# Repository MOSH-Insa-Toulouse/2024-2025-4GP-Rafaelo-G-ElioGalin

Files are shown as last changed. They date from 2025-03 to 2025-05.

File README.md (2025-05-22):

# 2024-2025-4GP-Rafaelo-G-ElioGalin

# Projet Capteur

## Somaire

- [Principe du Projet](#principe-du-projet)
- [Livrables](#livrables)
- [LTSpice](#ltspice)
- [Réalisation informatique du PCB sur KiCAD](#Realisation-informatique-du-pcb-sur-kicad)
- [Réalisation physique du PCB](#Réalisation-physique-du-PCB)
- [Code Arduino](#code-arduino)
- [Application](#application)
- [Datasheet](#datasheet)
- [Conclusion](#conclusion)
- [Auteurs](#auteurs)

## Contexte du Projet
Dans le Cadre du cours " Du capteur au banc de test", qui se base sur l'article "Pencil Drawn Strain Gauges and Chemiresistors on Paper" de Cheng-Wei Lin et al., les étudiants sont invités à caractériser un capteur particulier composé d'une simple feuille de papier et d'une couche de graphite. Cette couche de graphite joue le rôle d'une resistance variable qui dépend de la flexion du papier. Le but de ce projet est de réaliser un banc de test permettant d'étudier les variations de cette résistance en fonction de la déformation du capteur.

## Livrables

- Un PCB contenant différents modules se reliant à une carte Arduino UNO.
- Un code Arduino pour pouvoir controler les différents modules sur le PCB.
- Un application permettant la connection au PCB par Bluetooth.
- Une datasheet du capteur graphite.

## LTSpice 

La résistance du capteur graphite est de l'ordre du Méga Ohm et ne peut donc pas se mesurer simplemen. Nous utilison une alimentation 5V, nous avons donc :
U = R * I --> I = U/R --> I très faible.

Pour pouvoir obtenir des valeurs acceptables, nous avons réalisé un circuit amplificateur à transimpédance : 

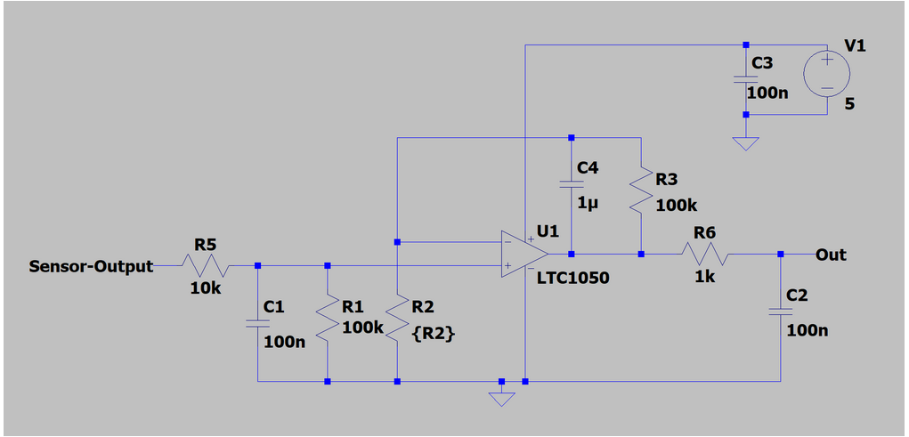
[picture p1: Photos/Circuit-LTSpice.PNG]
LTSpice-shema


Pour l'amplificateur opérationnel nécessaire au circuit, nous avons choisi le LTC1050 pour sa capacité à accepter un courant d'entrée faible et un offset de tension bas.

Afin d'améliorer le rapport Signal/Bruit, nous avons ajouté trois filtres : 

- filtre passe bas passif en entrée (R1,C1) avec une fréquence de coupure fc1 = 16Hz.
- filtre passe bas actif couplé à l'amplificateur opérationnel (R3,C4) avec une Fréquence de coupure fc2 = 1.6Hz. Ce filtre permet de s'isoler du bruit 50Hz du réseau électrique.
- filtre en sortie (R6,C2), avec une fréquence de coupure fc3 = 1.6kHz. Ce filtre permet de s'affranchir du bruit généré par notre circuit.

## Réalisation informatique du PCB sur KiCAD

Pour la réalisation du PCB, nous avons utilisé le logiciel KiCAD 6.0. Ce logiciel permet de créer le cricuit électrique ainsi que le PCB grâce à ses nombreuses librairies de composants.

La réalisation du PCB implique l'utilisation de différents modules qu'il faut pouvoir afficher sur le shéma : 

- Un module Bluetooth HC-05.
- Un écran OLED
- Un potentiomètre digital qui remplace la résistance R2 de notre circuit LTSpice.

Dans un premier temps, nous avons effectuée le shéma électrique : 

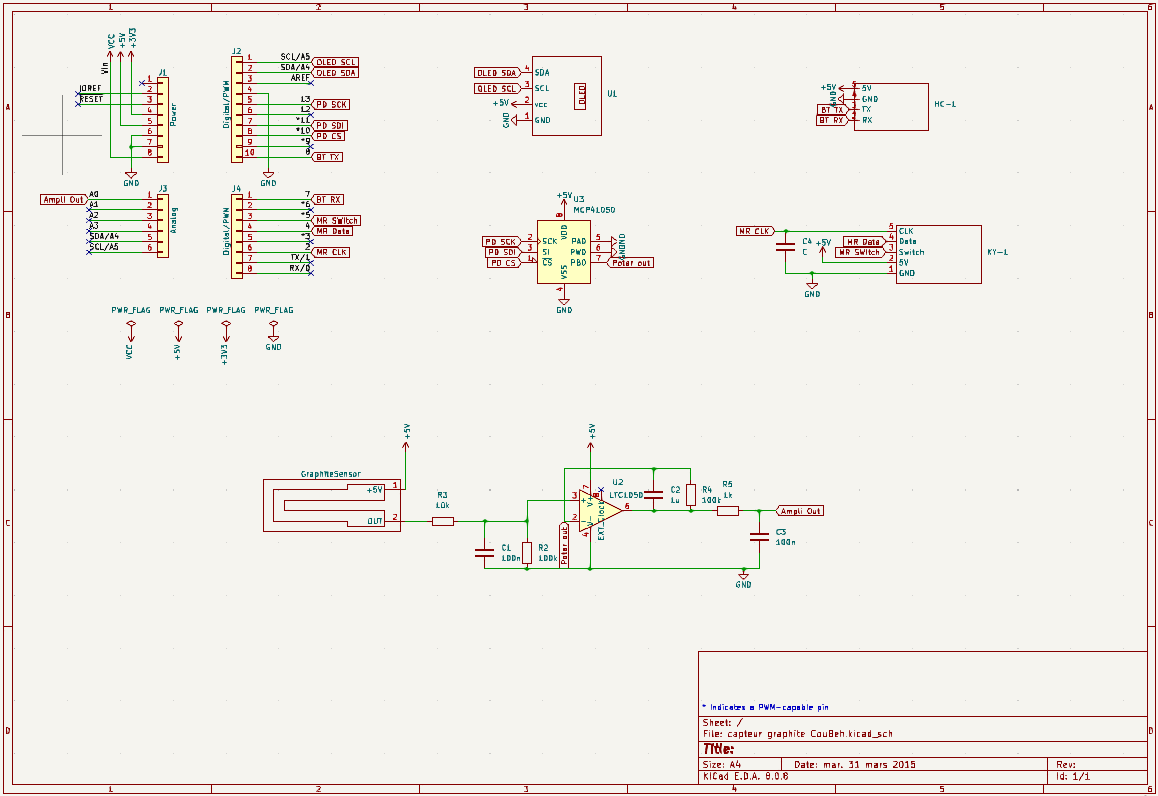
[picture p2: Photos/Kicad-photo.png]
kicad-shema


Dans un second temps, une fois tous les composants reliés entre eux, nous avons réalisé le PCB :

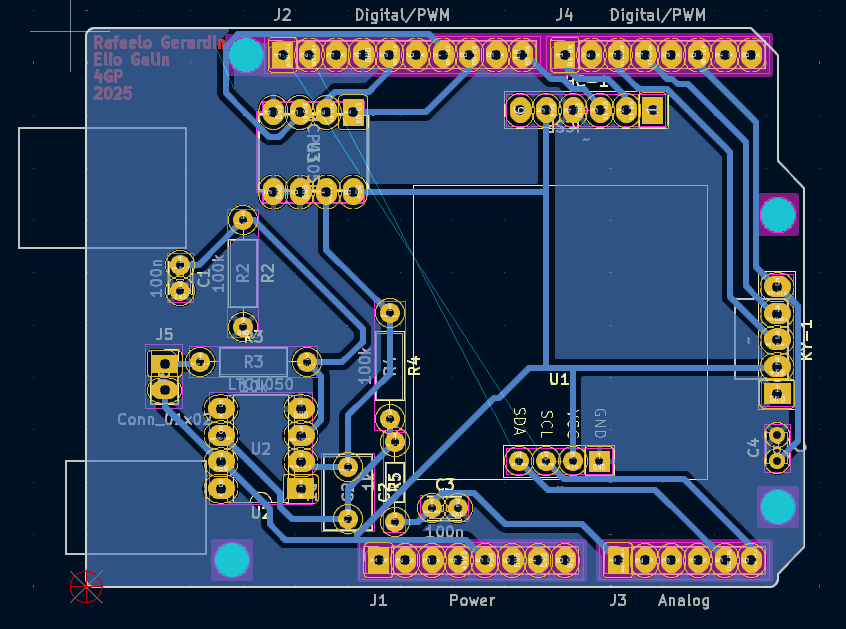
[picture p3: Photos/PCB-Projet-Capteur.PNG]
PCB-shema


Voici un visuel 3D du PCB pour donner une idée du placement des composants :

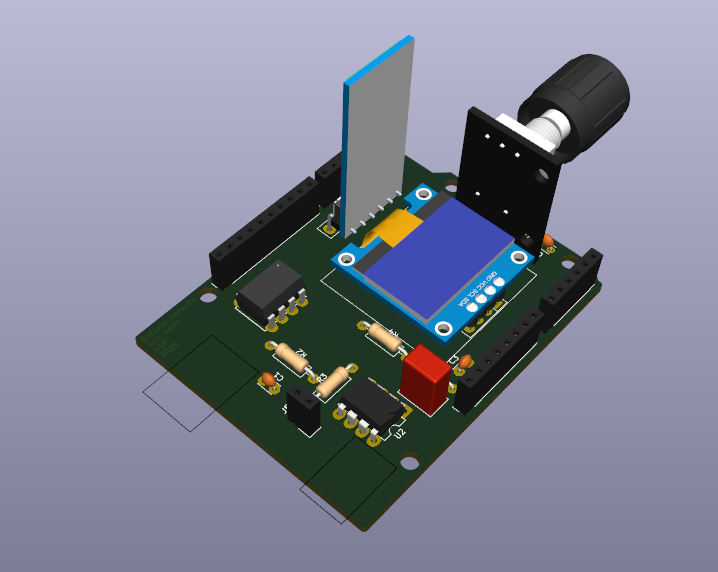
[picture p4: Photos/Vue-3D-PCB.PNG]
pcb-3d


Vous pouvez tout retrouver en détail dans le dossier [Kicad](/kicad/).

## Réalisation physique du PCB

Grâce à l'aide de Catherine Crouzet, nous avons pu fabriquer le PCB nous mêmes.

Pour ce faire, nous avons tout d'abord créé un fichier Gerber depuis KiCAD :

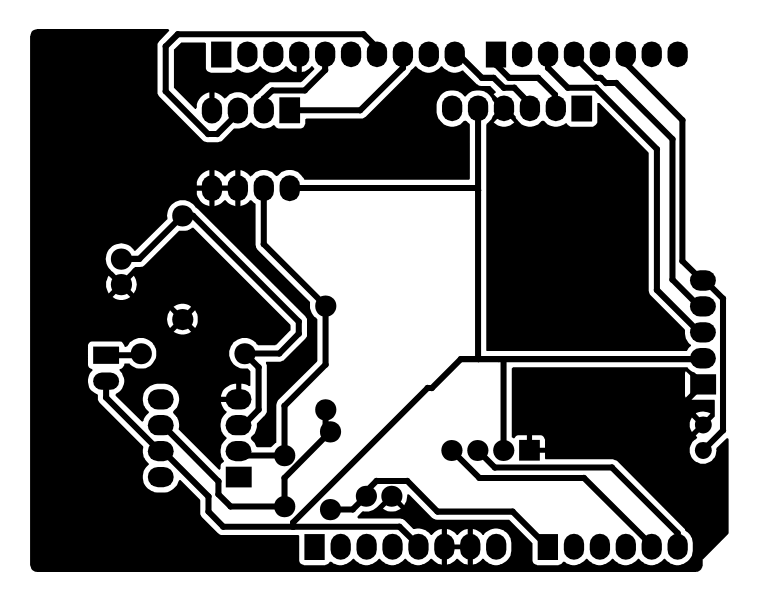
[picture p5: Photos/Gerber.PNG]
gerber


Ce filtre sert de masque de gravure. On place le masque sur une plaquette en epoxy jaune recouverte d'une fine couche de cuivre, elle même recouverte d'une couche de résine. Il sert de porotection pour la résine lors de son passage sous une lampe UV. Apres son passage sous la lampe à UV, la plaquette est déposé dans un bain "révélateur", qui retire la couche de résine qui a été en contact avec les UV, et aussi le cuivre en dessous de cette résine. Après un contrôle visuel pour s'assurer de la bonne exécution du processus, la plaque est retiré du bain et lavée à l'eau pour retirer le produit du bain et ensuite à l'acétone pour retirer la couche de résine qui a protégé les pistes en cuivre. Le PCB est maintenant près, on peut couper les parties non nécessaire de la carte pour un rendu plus propre.

Suite à ce processus, nous avons percé les trous dans lesquels des composants ainsi que des connecteurs des différents modules, puis nous les avons soudés.

## Code Arduino

Les differents modules sont contrôlés par un code Arduino 

Au branchement de l'Arduino UNO, après avoir envoyé le code, on peut voir sur l'écran OLED un menu déroulant:

-Menu 1 : Mesure Graphite
-Menu 2 : Infos Createurs

La navigation se fait avec l'encodeur rotatoir, le faire tourner permets de faire defiler les menus, et le cliquer permet d'accéder au menu sélectionné.

Vous trouverez le code Arduino [ici](/Code-Arduino/)

## Application

Nous avons utilisé  le site MIT App Inventor pour réalisé l'application qui reçoit et affiche en temps réel les valeurs mesurées par le Capeur graphite sur un graphe.

PHOTO

L'application est assez simple. Elle permet :
- De se connecter à un appareil via le bluetooth.
- De démarrer une acquisition et de la mettre en pause.
- d'effacer le graphe.
- De s'adapter en cas de changement de position du téléphone en offrant un mode paysage.

Vous la trouverez [ici](/Application Projet Capteur/)

## Datasheet

Nous avons écrit une datasheet qui caractérise le capteur graphite. Nous avons réalisé les mesures avec notre système et à l'aide d'un module 3D composé de demi-cercles permettant une déformation croissante précise.

Nous avons pu tracer ces courbes caractéristique de différents types de crayons (2H,HB,2B,4B,6B): 

Compression :

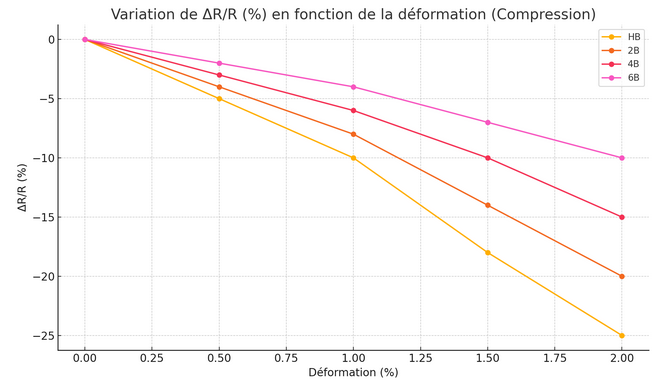
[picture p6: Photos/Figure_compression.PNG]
graphe de compression


Tension:

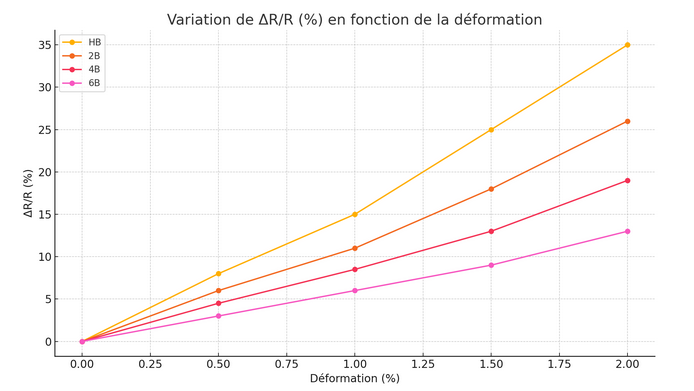
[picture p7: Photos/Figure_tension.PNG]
graphe de tension


Vous pouvez retrouver cette datasheet [ici](/Datasheet/)

## Conclusion

Tous nos résultats sont à  prendre avec prudence. Nous ne pouvons pas affirmer avoir réalisé un dépot de graphite parfaitement uniforme sur tous les capteurs, ce qui a pu avoir un impact important sur la valeur de leur résistance, et donc sur leur comprtement. De plus, la qualité du matériel utilisé n'est pas  optimale : les composants et les connexions présentent des imperfections qui ont pu influencer les mesures obtenues.

Cela dit, ce capteur présente plusieurs avantages : il est très versatile, peu coûteux, et extrêmement simple d’utilisation. L’électronique associée peut être facilement miniaturisée, et le capteur s’avère relativement sensible. Son principal défaut reste cependant l’homogénéité du dépôt de graphite. Si ce point pouvait être amélioré, le capteur pourrait être envisagé pour des applications industrielles, notamment pour des usages ponctuels, à grande échelle, ou à usage unique.
Dans un cadre personnel ou éducatif, ce capteur est particulièrement adapté. Il possède une forte valeur pédagogique, comme en témoigne ce projet, en permettant d’explorer de nombreux domaines scientifiques et techniques.

Ce capteur est-il industrialisable ? 

Oui et non.

Il pourrait trouver une application dans des secteurs comme l’aviation, où l’on utilise un très grand nombre de capteurs de contrainte. Son faible coût pourrait représenter un avantage économique. Néanmoins, ses limitations électroniques — notamment en termes de fiabilité et de miniaturisation — pourraient poser problème dans des environnements contraints.

Il pourrait en revanche être largement démocratisé dans le domaine de l’éducation, comme outil d’apprentissage ou de découverte.

Mais malgré son coût très faible, ce capteur reste très niche et la présence d’options plus performantes sur le marché rendent sa rentabilité à l'échelle industrielle peu crédible. Nous pensons donc qu’il serait difficilement industrialisable à grande échelle.

## Auteurs

Rafaëlo GERARDIN : <gerardin@insa-toulouse.fr>
Elio GALIN : <galin@insa-toulouse.fr>

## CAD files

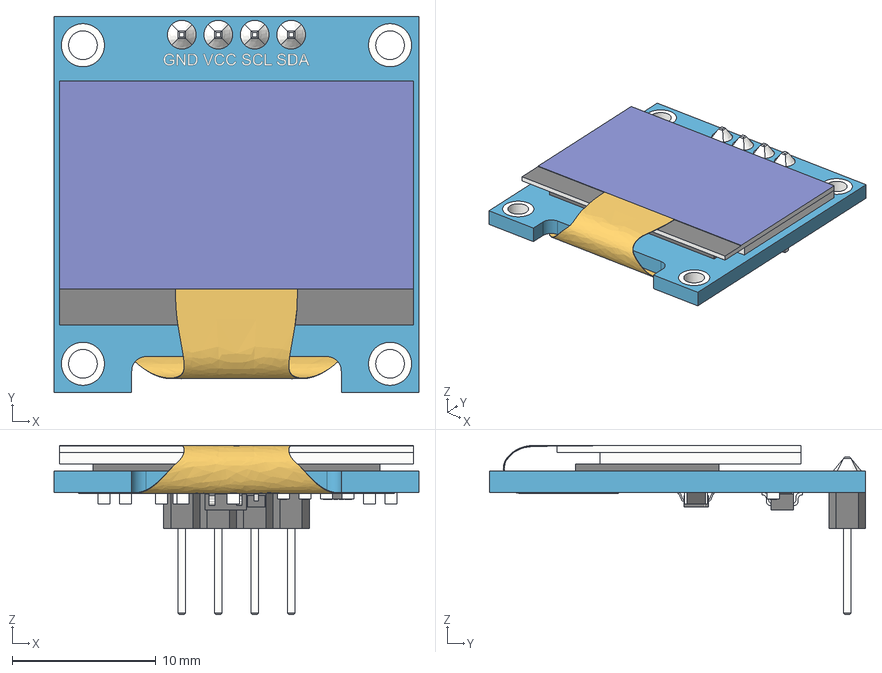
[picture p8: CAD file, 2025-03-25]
kicad/capteur graphite CouBeh/Models 3D/SSD1306_OLED_Display(128x64)(1).step
25.4 x 26.2 x 11.8 mm
board
screen
pin_header
soldering
smd_capacitor
smd_capacitor (1)
914_smd_resistor
472_smd_resistor x 3
t4_smd_diode
smd_capacitor (2)
smd_capacitor (3)
smd_capacitor (4)
smd_capacitor (5)
smd_capacitor (6)
472_smd_resistor (1)
SOT-23_XC6206 v3
smd_capacitor (7)
flat_cable

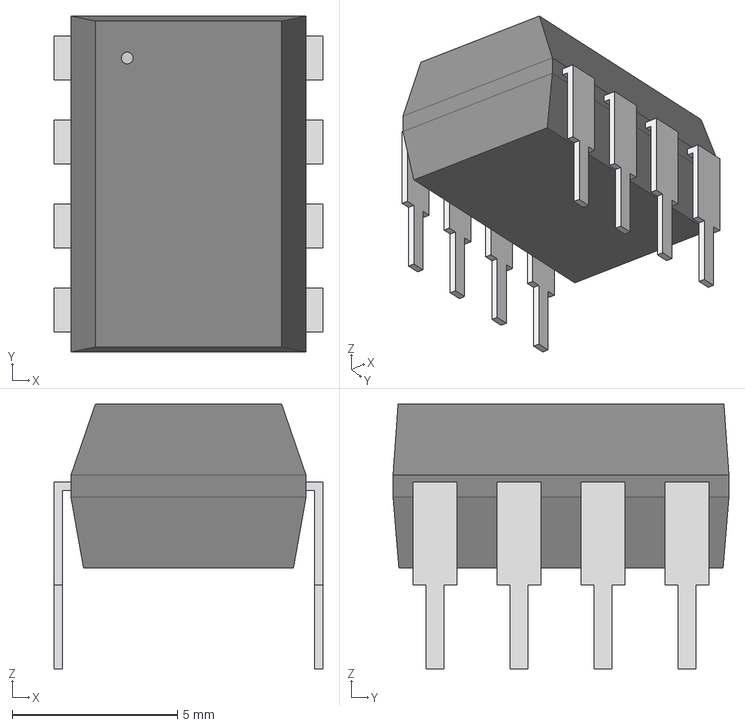
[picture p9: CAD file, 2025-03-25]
kicad/capteur graphite CouBeh/Models 3D/PDIP8_300MC_MCH.step
8.13 x 10.2 x 8.00 mm

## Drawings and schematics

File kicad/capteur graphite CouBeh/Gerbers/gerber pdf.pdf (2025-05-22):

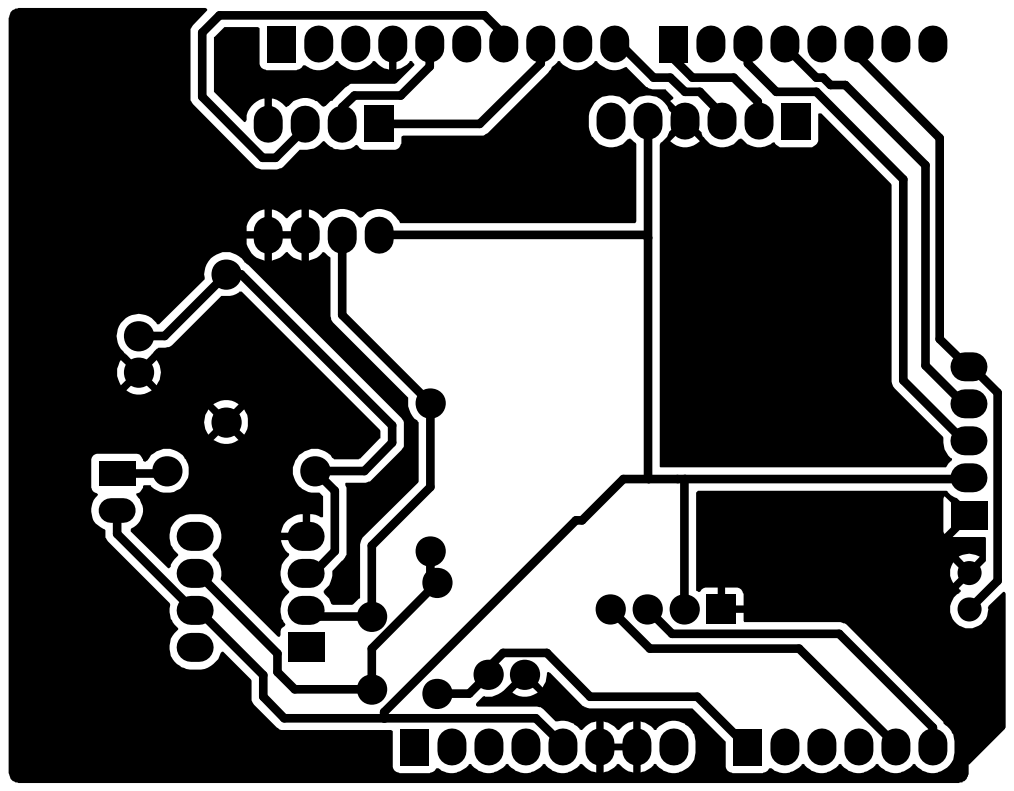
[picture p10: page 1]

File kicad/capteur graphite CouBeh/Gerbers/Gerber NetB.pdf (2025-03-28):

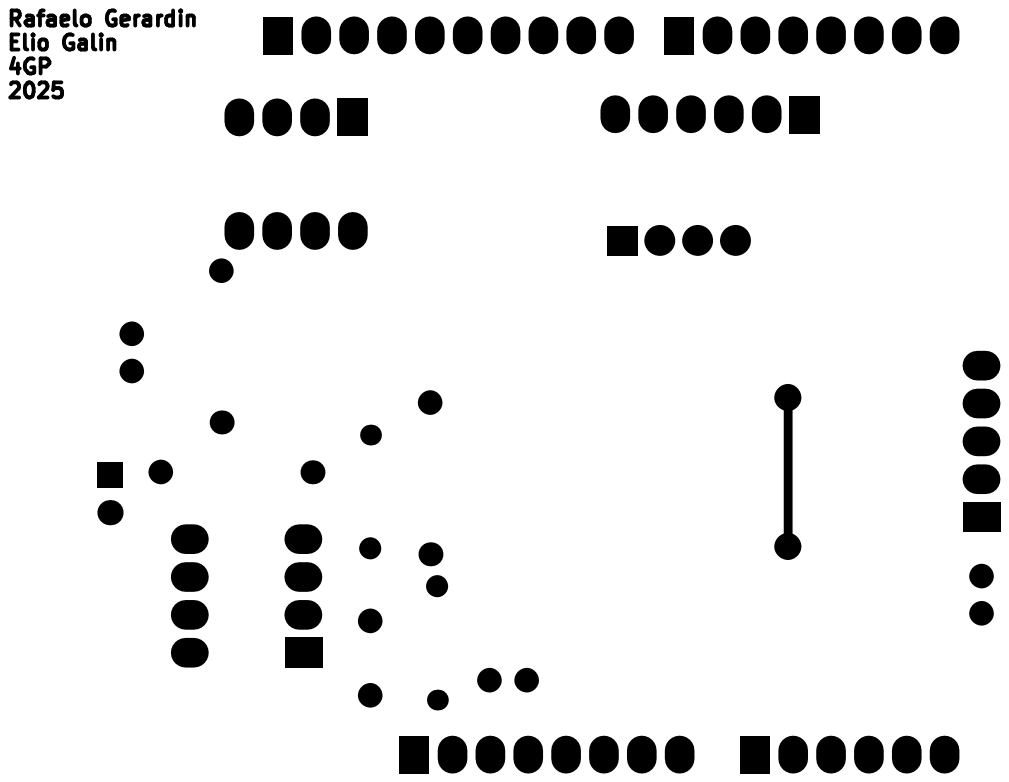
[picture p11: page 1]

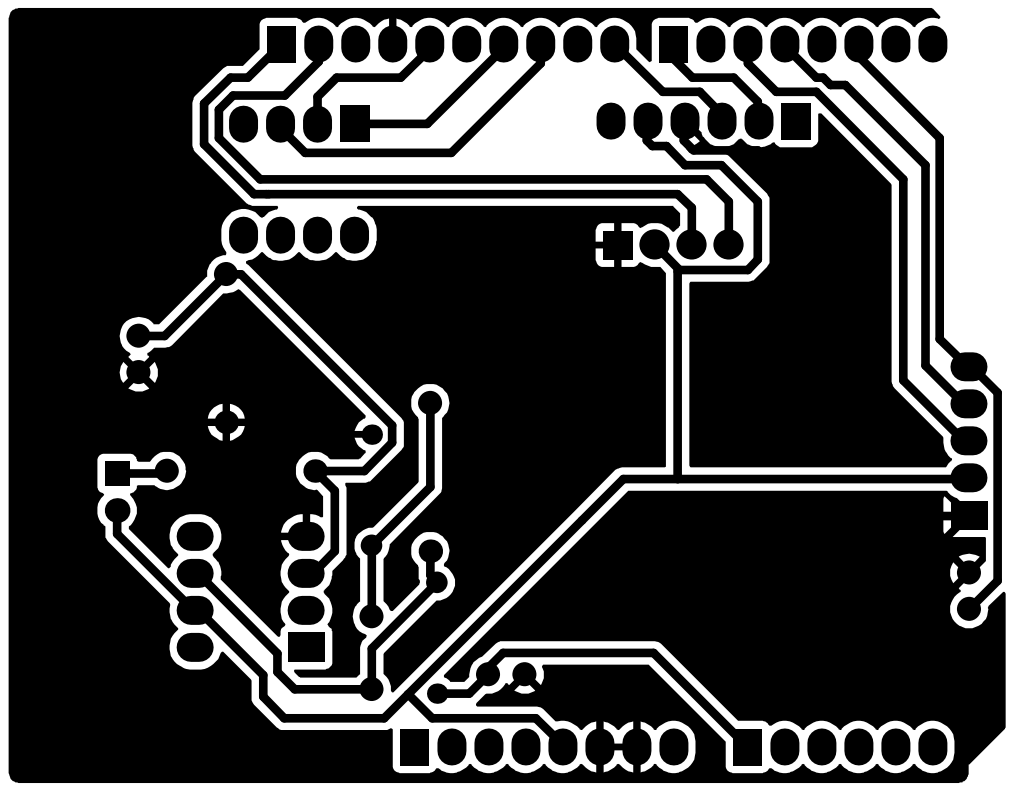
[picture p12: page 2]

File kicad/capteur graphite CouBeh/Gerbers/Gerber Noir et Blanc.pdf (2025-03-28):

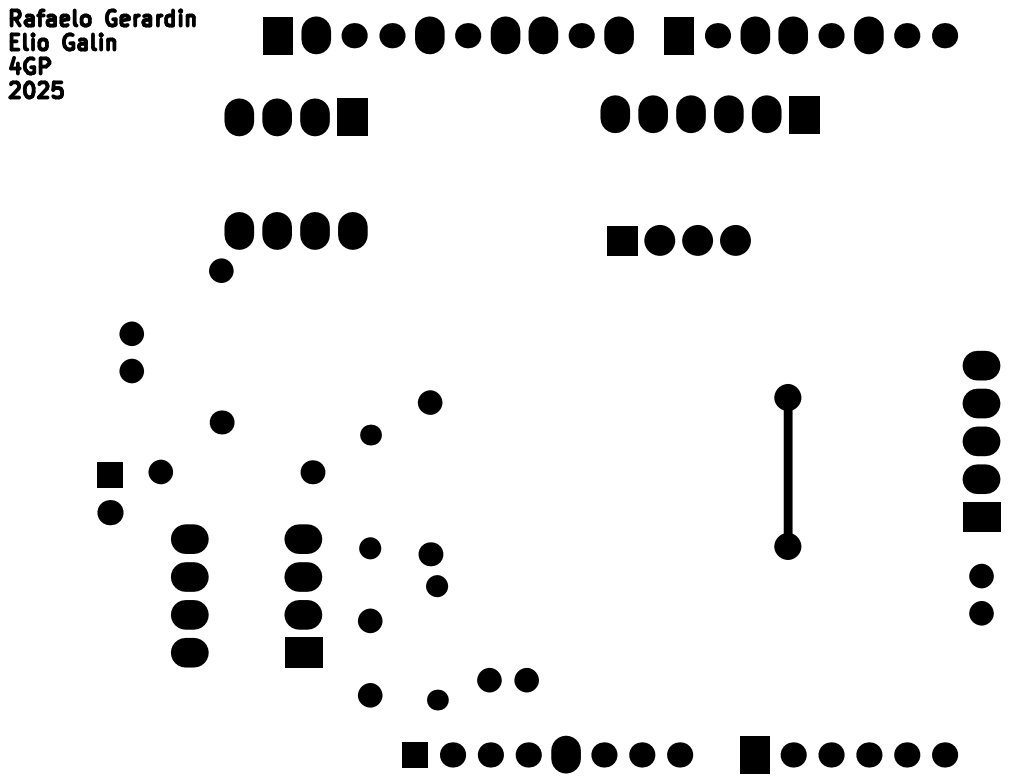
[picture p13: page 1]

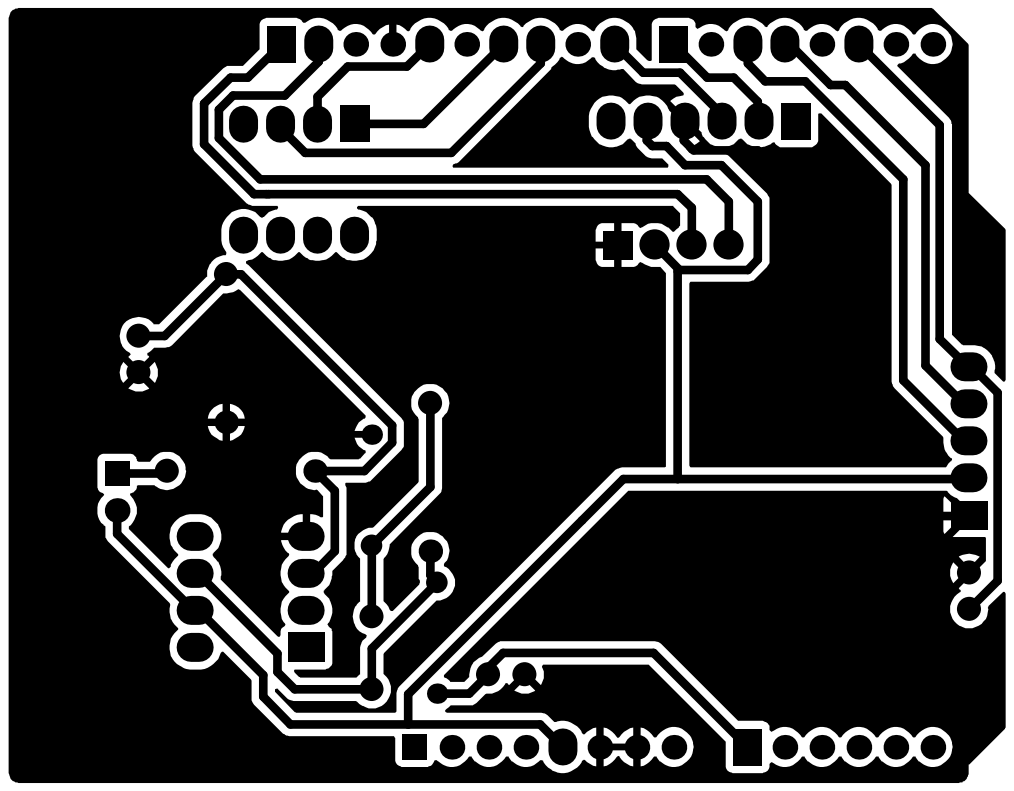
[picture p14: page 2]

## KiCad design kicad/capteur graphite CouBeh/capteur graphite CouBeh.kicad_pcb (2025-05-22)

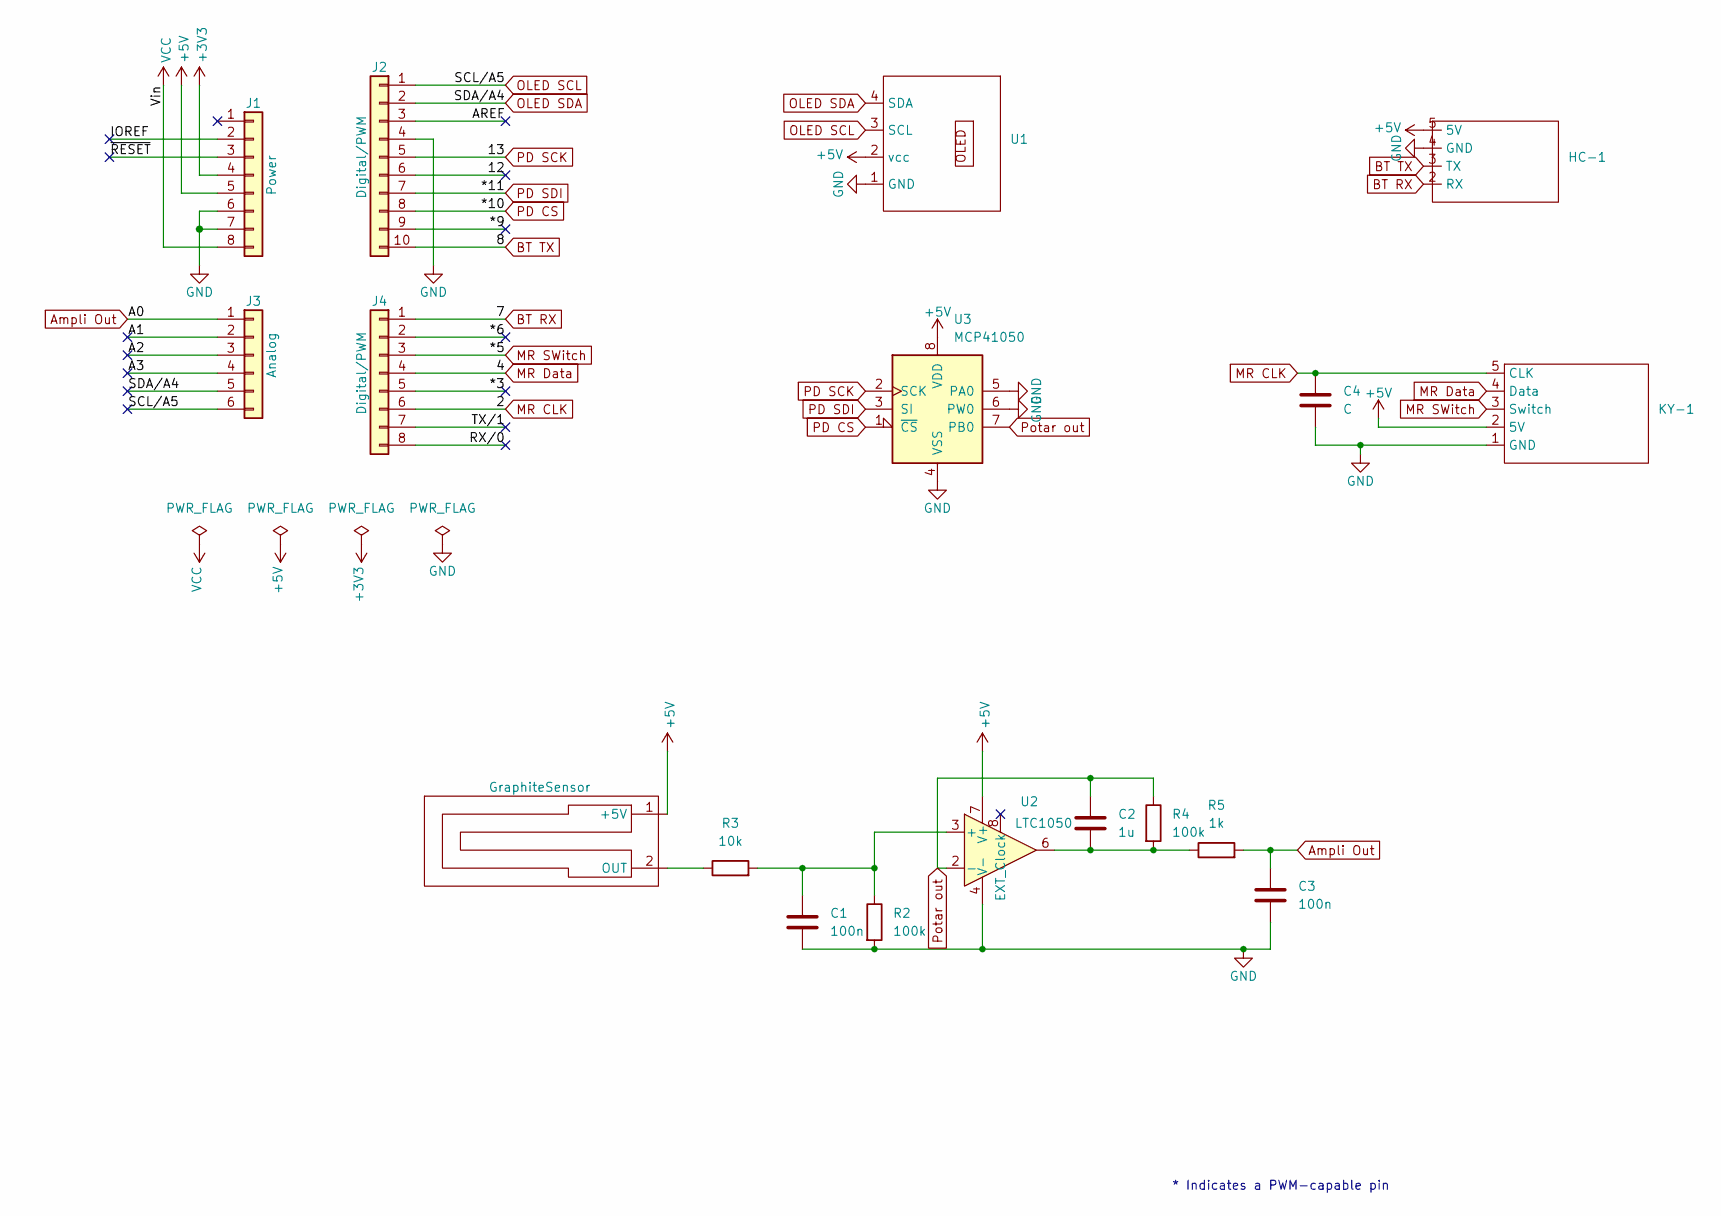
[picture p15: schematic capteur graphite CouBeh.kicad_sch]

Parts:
C1, C3: 100n; C_Disc_D3.0mm_W2.0mm_P2.50mm
C2: 1u; C_Rect_L7.0mm_W4.5mm_P5.00mm
C4: C; C_Disc_D3.0mm_W2.0mm_P2.50mm
GraphiteSensor: (no value)
HC-1: Module Bluetooth
J1: Power; PinSocket_1x08_P2.54mm_Vertical
J2: Digital/PWM; PinSocket_1x10_P2.54mm_Vertical
J3: Analog; PinSocket_1x06_P2.54mm_Vertical
J4: Digital/PWM; PinSocket_1x08_P2.54mm_Vertical
KY-1: Module Rotatoire
R2, R4: 100k; R_Axial_DIN0207_L6.3mm_D2.5mm_P10.16mm_Horizontal
R3: 10k; R_Axial_DIN0207_L6.3mm_D2.5mm_P10.16mm_Horizontal
R5: 1k; R_Axial_DIN0204_L3.6mm_D1.6mm_P7.62mm_Horizontal
U1: OLED
U2: LTC1050; DIP-8_W7.62mm
U3: MCP41050; PDIP8_300MC_MCH

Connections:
+3V3: J1.4
+5V: GraphiteSensor.1 (+5V), HC-1.5 (5V), J1.5, KY-1.2 (5V), U1.2 (vcc), U2.7 (V+), U3.8 (VDD); also elsewhere on the board
/12: J2.6
/*3: J4.5
/*6: J4.2
/*9: J2.9
/A1: J3.2
/A2: J3.3
/A3: J3.4
/AREF: J2.3
/IOREF: J1.2
/RX/0: J4.8
/TX/1: J4.7
/~RESET: J1.3
Ampli Out: C3.1, J3.1, R5.2
BT RX: HC-1.2 (RX), J4.1
BT TX: HC-1.3 (TX), J2.10
GND: C1.2, C3.2, C4.2, HC-1.4 (GND), J1.6, J1.7, J2.4, KY-1.1 (GND), R2.2, U1.1 (GND), U2.4 (V-), U3.4 (VSS), U3.5 (PA0), U3.6 (PW0)
MR CLK: C4.1, J4.6, KY-1.5 (CLK)
MR Data: J4.4, KY-1.4 (Data)
MR SWitch: J4.3, KY-1.3 (Switch)
unnamed: C2.2, R4.2, R5.1, U2.6
unnamed 22: GraphiteSensor.2 (OUT), R3.1; also elsewhere on the board
unnamed: C1.1, R2.1, R3.2, U2.3 (+)
OLED SCL: J2.1, J3.6, U1.3 (SCL)
OLED SDA: J2.2, J3.5, U1.4 (SDA)
PD CS: J2.8, U3.1 (~CS)
PD SCK: J2.5, U3.2 (SCK)
PD SDI: J2.7, U3.3 (SI)
Potar out: C2.1, R4.1, U2.2 (-), U3.7 (PB0)
VCC: J1.8

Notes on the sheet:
* Indicates a PWM-capable pin

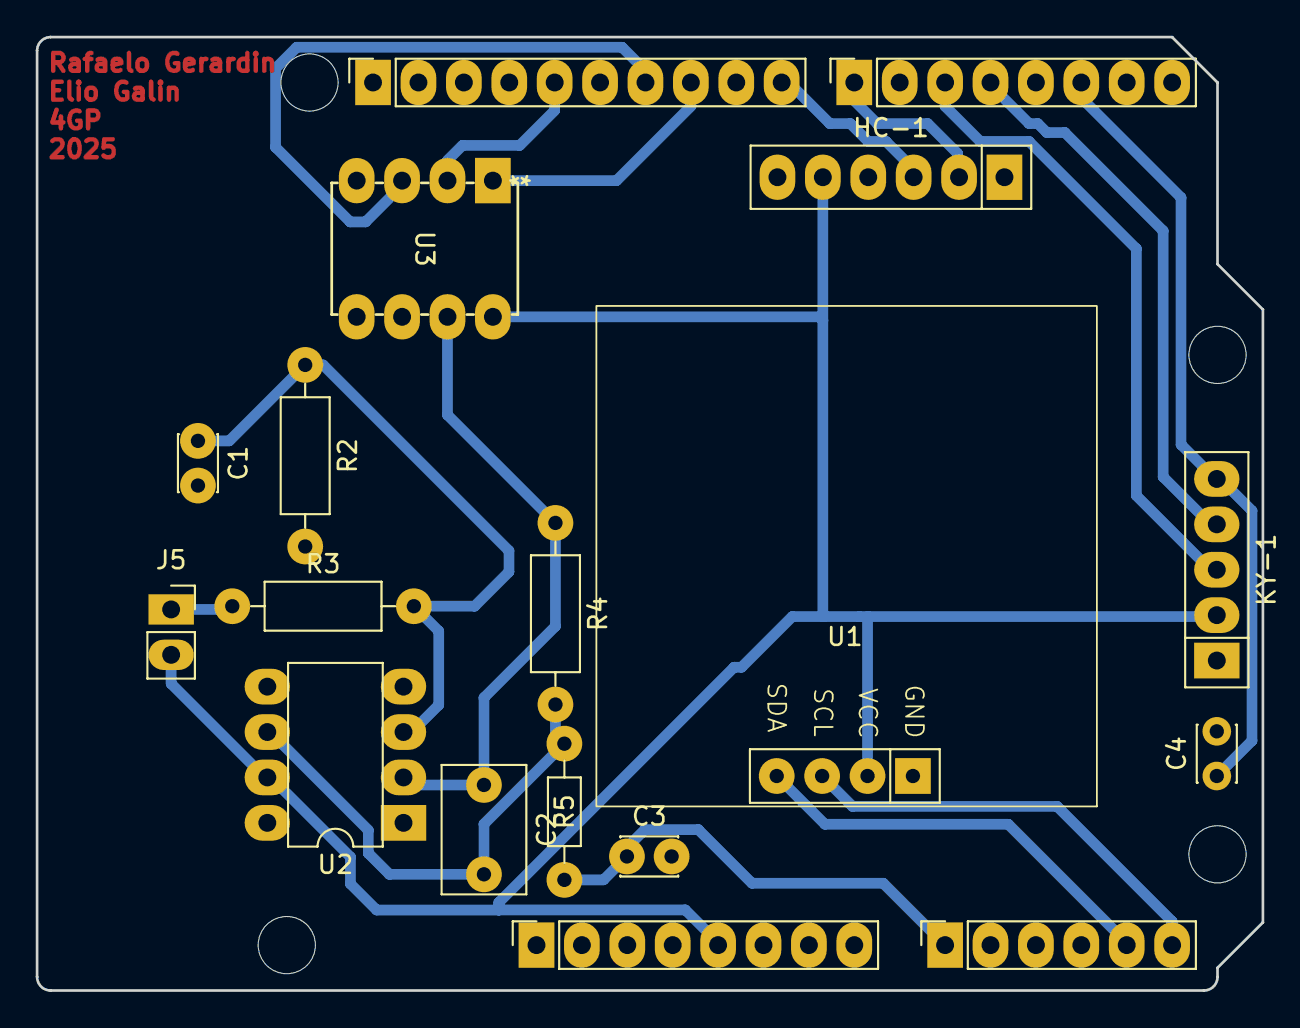
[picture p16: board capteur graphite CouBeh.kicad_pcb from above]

Board: 2 copper layers, 68.6 x 53.3 mm, 22 parts (0 on the bottom side), 17 nets.

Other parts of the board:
J5: Conn_01x02; PinSocket_1x02_P2.54mm_Vertical
MH1, MH2, MH3, MH4: MountingHole_3.2mm

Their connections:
+5V: J5.2; also elsewhere on the board
unnamed 22: J5.1; also elsewhere on the board

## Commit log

2025-02-21 Ajout de ma to-do list
2025-02-21 Ajout d'un item a la liste
2025-05-22 Rename Circuit LTSpice.PNG to Circuit-LTSpice.PNG
2025-05-22 Rename PCB Projet Capteur.PNG to PCB Projet-Capteur.PNG
2025-05-22 Rename PCB Projet-Capteur.PNG to PCB-Projet-Capteur.PNG
2025-05-22 Rename Vue 3D PCB.PNG to Vue-3D-PCB.PNG
2025-05-22 Create Code Arduino
2025-05-22 Update Code Arduino
